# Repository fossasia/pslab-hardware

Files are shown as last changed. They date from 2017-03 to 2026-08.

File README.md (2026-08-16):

# pslab-hardware





This repository contains the [PSLab](https://pslab.io) hardware design files. PSLab is a tiny pocket science lab that provides an array of test and measurement instruments for doing science and engineering experiments. It can function like an oscilloscope, waveform generator, frequency counter, programmable voltage and current source and also as a data logger. The first version of hardware (v1) was developed by [Jithin](https://github.com/jithinbp). Later versions were developed by [Padmal](https://github.com/CloudyPadmal) and [Rafael](https://github.com/RafaelLeeImg).

## PCB Layout
Front Side                        | Back Side
 -------------------------------- | ----------------------------------
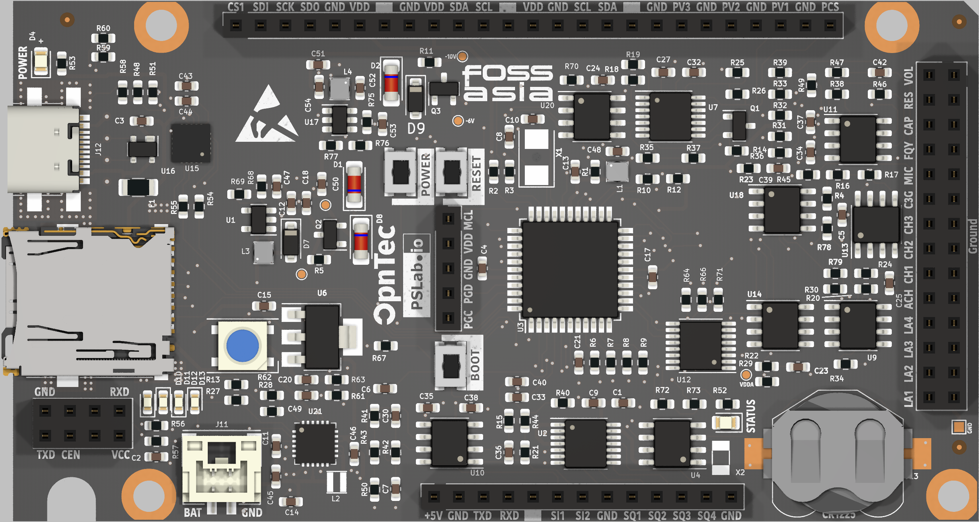
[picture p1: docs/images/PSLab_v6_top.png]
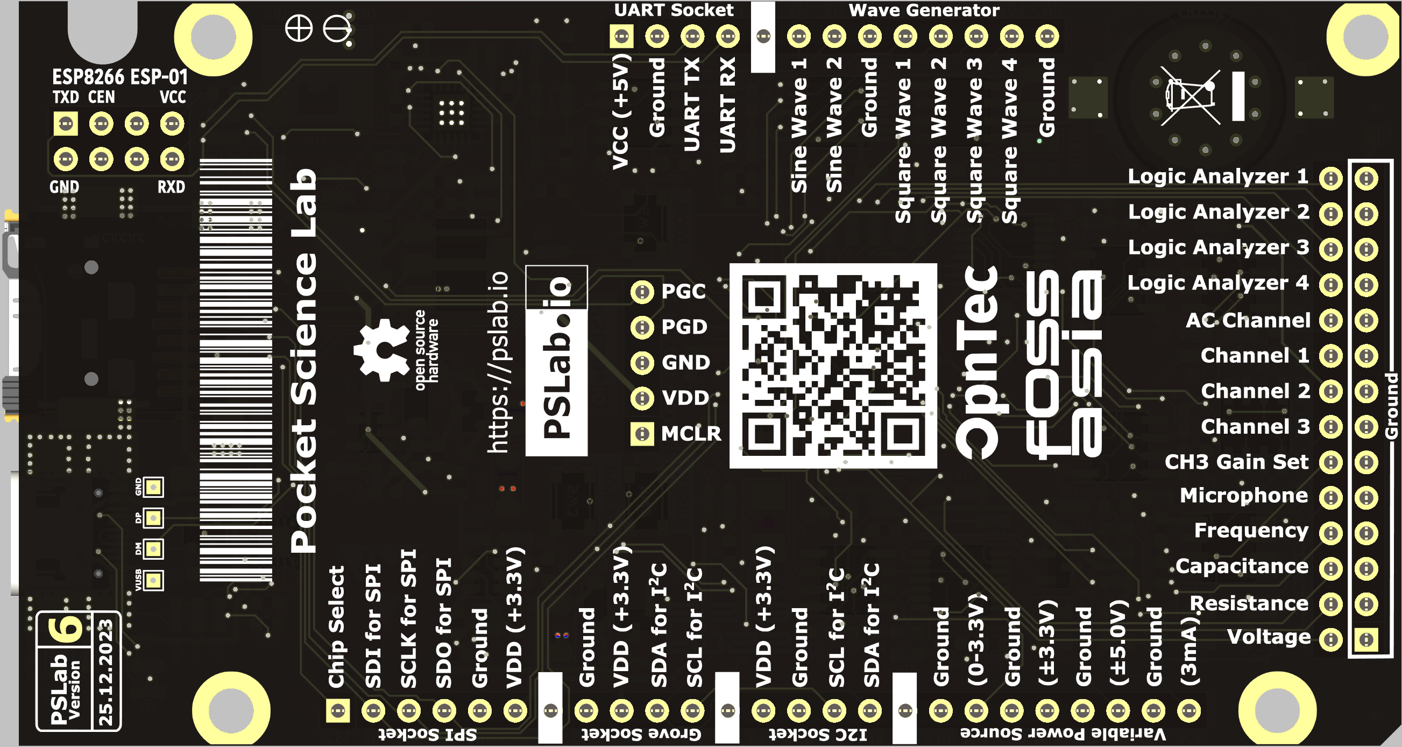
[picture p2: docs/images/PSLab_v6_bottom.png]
 | 

## Pin-outs
- Find the pin-out diagram of PSLab V6 [here](docs/pin_layouts/PSLab_Pin_Layout.pdf)!

## Applications and Firmware Source Repositories

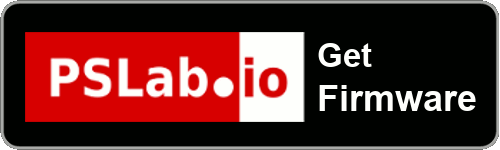
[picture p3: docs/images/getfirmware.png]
(https://github.com/fossasia/pslab-firmware)
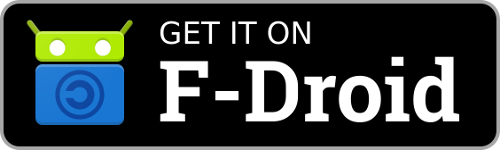
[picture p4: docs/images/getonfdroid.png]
(https://f-droid.org/en/packages/io.pslab/)
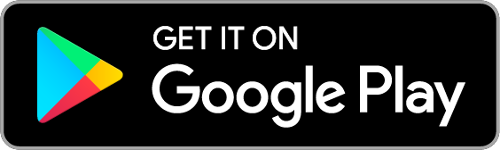
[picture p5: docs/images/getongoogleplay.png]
(https://play.google.com/store/apps/details?id=io.pslab)
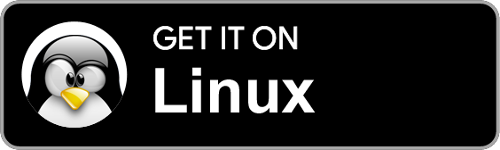
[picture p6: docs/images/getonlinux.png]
(https://github.com/fossasia/pslab-app/tree/app)
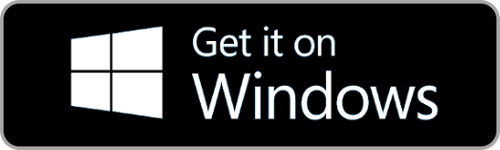
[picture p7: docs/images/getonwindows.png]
(https://github.com/fossasia/pslab-app/tree/app)
| 	|	| 	| 	| 	|
|---	|---	|---	|---	|---	|

The following software components are available:
* Bootloader: https://github.com/fossasia/pslab-bootloader
* Firmware: https://github.com/fossasia/pslab-firmware
* Python library: https://github.com/fossasia/pslab-python
* PSLab app: https://github.com/fossasia/pslab-app

## Buy Device

* You can get a Pocket Science Lab device from the [FOSSASIA Shop](https://fossasia.com).
* More resellers are listed on the [PSLab website](https://pslab.io/shop/).

## Communication

* Our chat channel is on Gitter here at [PSLab](https://gitter.im/fossasia/pslab)
* Mailing List https://groups.google.com/forum/#!forum/pslab-fossasia

## Repository Structure

```
📦pslab-hardware
 ┣ 📂archives                                   # Source files for previous PSLab versions
 ┃ ┣ 📂Breakout_Boards
 ┃ ┣ 📂PSLab KiCAD
 ┃ ┣ 📂PSLab KiCAD v2
 ┃ ┗ 📂PSLab KiCAD v3
 ┣ 📂docs                                       # Supplementary material
 ┃ ┣ 📂components
 ┃ ┃ ┣ 📜BillOfMaterials.csv                    # Component list
 ┃ ┃ ┗ 📜InteractiveBoM.html                    # Interactive version of BoM
 ┃ ┣ 📂datasheets                               # PDF datasheets for components used in PSLab
 ┃ ┣ 📂drawings                                 # CAD dimension drawings
 ┃ ┣ 📂images
 ┃ ┃ ┣ 📂pslab_version_previews
 ┃ ┃ ┣ 📜 ...
 ┃ ┃ ┗ 📜PSLab_v6_top.png
 ┃ ┣ 📂pin_layouts                              # Pin labels and specifications
 ┃ ┃ ┣ 📜PSLab_Pin_Layout.pdf
 ┃ ┃ ┗ 📜PSLab_Pin_Layout.svg
 ┃ ┣ 📂position_files
 ┃ ┃ ┗ 📜PositionFile.csv                       # Pick and place information
 ┃ ┣ 📂reference                                # TeX documentation (stale)
 ┃ ┗ 📂schematics
 ┃ ┃ ┗ 📜PSLab.pdf                              # Board schematic in PDF
 ┣ 📂output
 ┃ ┣ 📂Gerber                                   # Gerber files for the current board design
 ┃ ┗ 📂Images                                   # Images of the four copper layers
 ┣ 📂print                                      # Silk screen images
 ┃ ┣ 📂Back-Side-Images
 ┃ ┗ 📜Readme.md
 ┗ 📂schematics                                 # KiCAD project files
   ┣ 📂3DModels                                 # STEP 3D models
   ┣ 📂PSLab.pretty                             # Custom library files
   ┣ 📜 ...
   ┗ 📜PSLab.pro                                # Main project file
```

## Version Information

| Version | Content | Preview |
| -------------- | ------- | ------- |
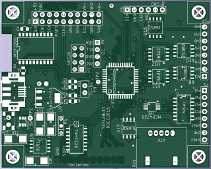
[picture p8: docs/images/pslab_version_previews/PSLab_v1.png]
| PSLab KiCAD v1   | Original version with `SEELABLET` schematics and layout files |  |
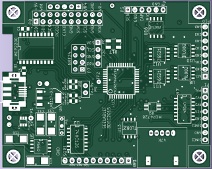
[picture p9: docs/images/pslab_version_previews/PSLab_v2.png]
| PSLab KiCAD v2 | Developed version with new additions (Voltage regulator, Oscillator) |  |
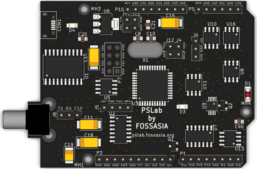
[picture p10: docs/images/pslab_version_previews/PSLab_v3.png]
| PSLab KiCAD v3 | Device layout changed to Arduino Uno form factor |  |
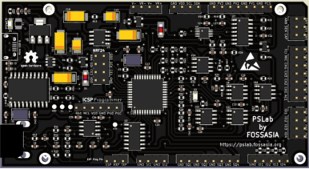
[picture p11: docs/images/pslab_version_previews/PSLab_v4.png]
| PSLab KiCAD v4 | Assembly optimized version with Arduino Mega form factor having components mounted only on top side |  |
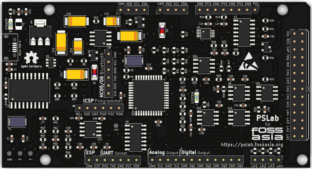
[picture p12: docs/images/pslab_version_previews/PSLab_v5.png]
| PSLab KiCAD v5 | Added socket for external bluetooth module and bottom silk screen with pin description |  |
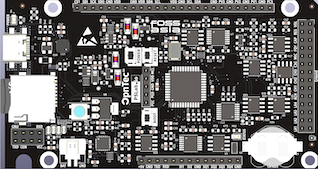
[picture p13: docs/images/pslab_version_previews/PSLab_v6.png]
| PSLab KiCAD v6 | Added external power input, RTC module, SD Card slot, USB type C, ESP 01 and upgraded UART and power ICs |  |

## Platform

* Microcontroller Platform : [PIC24EP256GP204](http://www.microchip.com/wwwproducts/en/PIC24EP256GP204)
* IDE: [MPLABX IDE v3.35](http://www.microchip.com/mplab/mplab-x-ide) (Supported on Linux/Windows/Mac)
* Compiler: [MPLAB® XC16 Compiler](http://www.microchip.com/mplab/compilers)
* Programming Tool: [PICkit™ 3 In-Circuit Debugger](http://www.microchip.com/Developmenttools/ProductDetails.aspx?PartNO=PG164130)

## Parts list

* [PIC24EP256GP204](http://www.microchip.com/wwwproducts/en/PIC24EP256GP204) - Microcontroller
* [MCP6S21](http://www.microchip.com/wwwproducts/en/mcp6s21) - Programmable gain amplifier
* [MCP4728](http://www.microchip.com/wwwproducts/en/mcp4728) - 4 Channel DAC
* [TC7660](http://www.microchip.com/wwwproducts/en/TC7660) - Charge Pump voltage invertor
* [TC1240A](http://www.microchip.com/wwwproducts/en/TC1240A) - Charge Pump voltage doubler
* [TL082](http://www.ti.com/product/TL082) - 2 channel Op-Amp
* [LM324](http://www.ti.com/product/LM324) - 4 channel Op-Amp
* [DS1307Z+](https://datasheets.maximintegrated.com/en/ds/DS1307.pdf) - RTC module
* [LDFM33PUR](https://www.st.com/resource/en/datasheet/ldfm.pdf) - 3.3 V regulator
* [LDL212PU50R](https://www.st.com/resource/en/datasheet/ldl212.pdf) - 5.0 V regulator
* [CP2102N-A02-GQFN24](https://www.silabs.com/documents/public/data-sheets/cp2102n-datasheet.pdf) - USB-UART bridge
* [74HC126](http://www.ti.com/product/SN74HC126) - 4 channel buffer
* [SP0503BAHTG](https://m.littelfuse.com/~/media/electronics/datasheets/tvs_diode_arrays/littelfuse_tvs_diode_array_sp05_datasheet.pdf.pdf) - ESD protector

* 0.5 A Fuse
* Assorted resistors, capacitors & diodes

Find the complete bill of materials from [this link](docs/components/BillOfMaterials.csv).

### Optional Parts

Extension slots for an ESP is available.
* [ESP8266 (ESP-01)](http://www.microchip.ua/wireless/esp01.pdf) - UART-TCP bridge

## Hardware Specs

* 3-Channel up to 2MSPS Oscilloscope. Software selectable amplification stages
* 12-bit Voltmeter with programmable gain. Input ranges from +/-10 mV to +/-16 V
* 3x 12-bit Programmable voltage sources +/-3.3 V,+/-5V,0-3 V
* 12-bit Programmable current source. 0-3.3 mA
* Supports Advanced plugins/Add-on Modules
* 4-Channel, 4 MHz Logic Analyzer
* 2x Sine/Triangular wave generators. 5 Hz to 5 KHz. Manual amplitude control for SI1
* 4x PWM generators. 15 nS resolution. Up to 8 MHz
* Capacitance Measurement. pF to uF range
* I2C, SPI and UART data buses for Accelerometer gyroscope humidity and temperature sensor modules etc

## Feature list for the acquisition and control

### Oscilloscopes

One of the main features of PSLab is the 3-channel Oscilloscope which can monitor analog inputs at maximum of 2 million samples per second. It includes controls such as triggering, and gain selection. Uses Python-Scipy for curve fitting.

### Waveform Generators

* SI1 : 5 Hz – 5 KHz arbitrary waveform generator. Manual amplitude control up to +/-3 Volts
* SI2 : 5 Hz – 5 KHz arbitrary waveform generator. Amplitude of +/-3 Volts. Attenuable via software
* SQx : There are four phase correlated PWM outputs with maximum frequency 32 MHz, 15 nano second duty cycle, and phase difference control.

### Measurement Functions

* Frequency counter tested up to 16 MHz.
* Capacitance Measurement. pF to uF range
* PSLab has several 12-bit analog inputs (function as voltmeters) with programmable gains, and maximum ranges varying from +/-5 mV to +/-16 V.

### Voltage and Current Sources

* 12-bit Constant Current source. Maximum current 3.3 mA (subject to load resistance).
* PSLab has three 12-bit Programmable voltage sources +/-3.3 V,+/-5 V,0-3 V. (PV1, PV2, PV3) controls

### Other useful tools

* 4MHz, 4-channel Logic analyzer with 15 nS resolution. Voltage and current sources
* SPI, I2C and UART outputs
* Graphical Interfaces for Oscilloscope, Logic Analyser, streaming data and several experiments developed that use a common framework which drastically reduces code required to incorporate control and plotting widgets.
* PSLab also has space for an ESP-01 module for WiFi access with access point/station mode.

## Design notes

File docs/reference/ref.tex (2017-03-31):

%----------------------------------------------------------------------------------------
%	PACKAGES AND OTHER DOCUMENT CONFIGURATIONS
%----------------------------------------------------------------------------------------

\documentclass[11pt,article,sans]{moderncv} % Font sizes: 10, 11, or 12; paper sizes: a4paper, letterpaper, a5paper, legalpaper, executivepaper or landscape; font families: sans or roman
\moderncvstyle{classic} % CV theme - options include: 'casual' (default), 'classic', 'oldstyle' and 'banking'
\moderncvcolor{blue} % CV color - options include: 'blue' (default), 'orange', 'green', 'red', 'purple', 'grey' and 'black'

\usepackage[scale=0.75]{geometry} % Reduce document margins

%\setlength{\hintscolumnwidth}{3cm} % Uncomment to change the width of the dates column
%\setlength{\makecvtitlenamewidth}{10cm} % For the 'classic' style, uncomment to adjust the width of the space allocated to your name

\usepackage{graphicx}
\usepackage{multicol}
\usepackage{changepage}

%----------------------------------------------------------------------------------------
%	NAME AND CONTACT INFORMATION SECTION
%----------------------------------------------------------------------------------------

\firstname{PSLab} % Your first name
\familyname{} % Your last name

\title{Technical Specifications}
\email{Mfd by. csparkresearch@gmail.com}
\address{www.fossasia.org}{}
\photo[100pt][0pt]{pictures/logo.png} % The first bracket is the picture height, the second is the thickness of the frame around the picture (0pt for no frame)

%----------------------------------------------------------------------------------------
\setlength\arrayrulewidth{.4pt}
\setlength\tabcolsep{6pt}

\begin{document}

\makecvtitle % Print the CV title

\chapter{\color{blue!50!green}\LARGE\bfseries Introduction}
\vspace{5mm}
\\.
\setlength{\parindent}{1cm}
\textit{\color{blue!20!black!80}PSLab provides an array of test equipment that includes an oscilloscope, waveform generators, frequency counters, Programmable voltage sources and many more for the curious ones among us. The measurement/control functions are accessible from the Python programming language and GUI applications are also available for a variety of science and engineering experiments. } .\\
\setlength{\parindent}{0cm}

%----------------------------------------------------------------------------------------
%	Pin definition section
%----------------------------------------------------------------------------------------

\vspace{20pt}
\chapter{\color{blue!50!green}\LARGE\bfseries Pin Definitions and Functions}
\section{Analog Inputs - Measure Voltages with 12-bit resolution}
\cventry{CH1}{Range:$\pm$ 16}{}{ Gain:up to 32x.}{ }{}{}
\cventry{CH2}{Range:$\pm$ 16}{}{ Gain:up to 32x.}{ }{}{}{}
\cventry{CH3}{Range:$\pm$ 3.3V}{}{}{}{*manual gain control by grounding Rg via resistor R  . $gain = 1 + \frac{10K}{R_g}$}{}
\cventry{MIC}{Range: $\pm15mV$}{}{}{ Gain:200x.}{}{}
\cventry{SEN}{Range: $0 - 3.3V$}{}{}{ Internally Pulled up to 3.3V via 5.1KOhm resistor}{}{}

\section{Analog Outputs}
\subsection{Waveform Generators}
\cventry{WG1}{5Hz to 5KHz Arbitrary Waveform Generator}{Range: $ \pm 3V$ .Attenuable}{}{}{}{}
\cventry{WG2}{5Hz to 5KHz Waveform Generator}{Range: $ \pm 3V$  }{}{}{}{}
\subsection{Programmable Voltage and Current Sources (12-bit)}
\cventry{PVS1}{Range: $ \pm 5V$}{}{Up to 10mA}{}{}{}
\cventry{PVS2}{Range: $ \pm 3.3V$}{}{Up to 10mA}{}{}{}
\cventry{PVS3}{Range: $0 - 3.3V$}{}{Up to 10mA}{}{}{}
\cventry{PCS}{Range: $0 - 3.3mA$}{}{}{}{Subject to Load resistance. Up to 3.3V voltage drop}{}

\section{Digital Inputs - Measure Logic Levels with 15nS resolution}
\subsection{Logic Analyzer, Frequency Counter, Timing Functions}
\cventry{ID1}{Range: $0 - 5V$}{}{0-32MHz}{}{}{}
\cventry{ID2}{Range: $0 - 5V$}{}{0-32MHz}{}{}{}
\cventry{ID3}{Range: $0 - 5V$}{}{0-32MHz}{}{}{}
\cventry{ID4}{Range: $0 - 5V$}{}{0-32MHz}{}{}{}
\cventry{Fin}{Range: Up to $\pm5V$}{}{0-16MHz}{}{}{}

\section{Digital Outputs }
\subsection{4x PWM output with 15nS frequency, phase, and DCycle control}
\cventry{SQR1}{Range: $0 - 5V$}{}{}{}{}{}
\cventry{SQR2}{Range: $0 - 5V$}{}{}{}{}{}
\cventry{SQR3}{Range: $0 - 5V$}{}{}{}{}{}
\cventry{SQR4}{Range: $0 - 5V$}{}{}{}{}{}

\section{Data Buses - I2C , SPI, UART}
\subsection{I2C (Inter-Integrated Circuit) Master: Up to 4MHz Clock speed}
\cventry{Vdd}{3.3V Power output}{}{}{}{}{}
\cventry{GND}{Return path}{}{}{}{}{}
\cventry{SCL}{I2C Clock Output}{}{}{}{}{}
\cventry{SDA}{I2C Data Line}{}{}{}{}{}

\subsection{SPI(Serial-Peripheral Interface) Master: Available on the 20-pin Expansion Slot. Supports all four modes of operation.}
\cventry{SCK}{SPI Clock Output}{}{Tested Up To 16MHz}{}{}{}
\cventry{SDO}{SPI Data Output (MOSI)}{}{}{}{}{}
\cventry{SDI}{SPI Data Input (MISO)}{}{}{}{}{}
\cventry{CS1}{Chip Select 1}{}{}{}{}{}
\cventry{CS2}{Chip Select 2}{}{}{}{}{}

\section{A Few Definitions For The Expansion slot}
\cventry{CLK}{16MHz , 0-3.3V TTL output}{}{This is also the reference clock for the 0-2MHz sine/triangle wave generator, and can be used to create phase correlated wavegen add-ons}{}{}{}
\cventry{AN8}{Analog Input}{}{Range: $0 - 3.3V$}{}{}{}

\section{Additional Nomenclature }
\cventry{GND}{Short for GROUND.}{}{This is the reference voltage, and is taken as 0 volts}{}{It is also connected to the ground level of the power source (power adapter)}{}
\cventry{V+/V-}{Power Outputs}{}{$\pm 9V$ . Current limit 20mA per channel}{}{}{}

\pagebreak
\vspace{20pt}
\chapter{\color{blue!50!green}\LARGE\bfseries Sensors and Add ons}\\

\section{Plug and Play Sensors}

\begin{adjustwidth}{7em}{0pt}

\begin{itemize}
\item MPU6050 : 3-Axis Accelerometer , 3-Axis GyroScope, temperature sensor
\item HMC5883L : 3-Axis Magnetometer with adjustable ranges
\item MLX90614 : Passive IR temperature sensor
\item BMP180 : Pressure , Temperature and Altitude module.
\item TSL2561 : Luminosity measurements up to 40K Lux
\item BH1750 : Luminosity measurements up to 40K Lux
\item SHT21 , Si7021 : Ambient Temperature and Humidity Module
\item SSD1306 : 128x64 OLED Display
\item HCSR501 : Passive IR module for motion sensing
\item AD9833 : 28-bit DDS function generator
\item PT100 temperature sensor, MQ Series Gas sensors
\item DSM501 : PM2.5 Dust Sensor
\item YL-69 : Hygrometer for soil humidity measurements
\item WS2812B RGB LED with 16 million shades 
\item HX711 24-bit differential ADC with 128x PGA
\item MFRC522 : RFID Reader
\item HB100 : 10.25GHz Doppler Radar
\end{itemize}
\end{adjustwidth}

\section{Wireless Subunits : 3-Byte addresses [ Purchase separately]}

PSLab has an On-board Transceiver (2-way radio link) Capable of communicating with multiple wireless nodes to control and receive sensor data payloads.\\ These wireless nodes are drop-in replacements for sensors, and have a typical line of sight range of 50 meters.

\begin{center}

%  \includegraphics[width=0.6\linewidth]{pictures/node_case.jpg}

\end{center}

\cventry{I2C}{Data bus for Interfacing with commonly available sensors.}{ Measure physical parameters with minimal mechanical interference}{}{}{}
\cventry{SPI}{Two Chip select pins}{}{}{}{}
\cventry{RGB out}{Control WS2812B arrays }{}{Daisy chained RGB LEDs with 16 million shades each}{}{}{}

\section{Control And Measurement Equipment Specifications}

\textit{\color{blue!50!green}Calibrated Against Professional equipment for high accuracy}\\
\begin{tabular}{|l|l|l|l}
\hline
\multicolumn{1}{|c|}{{\color[HTML]{9A0000} \textbf{Feature}}}          & \multicolumn{1}{c|}{{\color[HTML]{9A0000} \textbf{Description}}}                                                                                                                                                                                                                                                                                                             & \multicolumn{1}{c|}{{\color[HTML]{9A0000} \textbf{Socket Labels}}}                            & \multicolumn{1}{c}{{\color[HTML]{9A0000} \textbf{Range}}}                                                                                                            \\ \hline
\textbf{Analog Inputs}                                                 & \begin{tabular}[c]{@{}l@{}}Up to 6 analog inputs with various voltage ranges.\\ Programmable gain control.\\ 12-bit voltage measurement. Up-to 2MSPS sampling.\\ $3.3V$ Voltage Reference\\ \\ .\end{tabular}                                                                                                                                                    & \begin{tabular}[c]{@{}l@{}}CH1, CH2\\ CH3\\ MIC\\ SEN\end{tabular}                            & \multicolumn{1}{l|}{\begin{tabular}[c]{@{}l@{}}$\pm16 Volts$\\ $\pm3.3 Volts$\\ $\pm15m V V$\\ $0-3.3 V$\end{tabular}}                                               \\ \hline
\textbf{Analog Outputs}                                                & \begin{tabular}[c]{@{}l@{}}Programmable Voltage Sources (12-bit)\\ \\ \\ Programmable Constant Current Source\\ .\end{tabular}                                                                                                                                                                                                                                               & \begin{tabular}[c]{@{}l@{}}PVS1\\ PVS2\\ PVS3\\ PCS\\ .\end{tabular}                          & \multicolumn{1}{l|}{\begin{tabular}[c]{@{}l@{}}$\pm5 V$\\ $\pm3.3 V$\\ $0-3.3 V$\\ $0-3.3 mA$\\ .\end{tabular}}                                                      \\ \hline
\textbf{Digital Inputs}                                                & \begin{tabular}[c]{@{}l@{}}4 x TTL compatible digital Inputs. \\ Logic Analyzer\\ Frequency Counter (0-16MHz), \\ time measurement routines\\ \textit\{$\pm30ppm , 12MHz$ Reference oscillator\}\end{tabular}                                                                                                                                                               & \begin{tabular}[c]{@{}l@{}}ID1 - ID4\\ \\ Fin\end{tabular}                                    & \multicolumn{1}{l|}{\begin{tabular}[c]{@{}l@{}}$0-5$ V\\ \\ $0-\pm5 V$\end{tabular}}                                                                                 \\ \hline
\textbf{\begin{tabular}[c]{@{}l@{}}Waveform\\ Generators \end{tabular}} & \begin{tabular}[c]{@{}l@{}}Wavegen 1 (Sine/Triangle/Arbitrary)\\ -Frequency\\ -Amplitude. Manually attenuable \\ \\ Wavegen 2 (Sine/Triangle/Arbitrary)\\ --Frequency\\ -Amplitude. Fixed\\ \\ 4 x Phase Correlated Square Waves\\ -Frequency\\ -Phase difference maximum resolution\\ -Duty Cycle maximum resolution\\ -Also functions as simple state selectable output.\\ -servo/stepper motor control supported\end{tabular} & \begin{tabular}[c]{@{}l@{}}W1\\ \\ \\ \\ W2\\ \\ \\ \\ SQ1 - SQ4\\ \\ \\ \\ \\ .\end{tabular} & \multicolumn{1}{l|}{\begin{tabular}[c]{@{}l@{}}\\ $5-5K$Hz\\ $\pm3 V$\\ \\ \\ $5-5K$Hz\\ $\pm3 V$\\ \\ \ \\ $0-5 Volts$\\10Hz - 16MHz\\ 15nS\\ 15nS\\ \\ \\ .\end{tabular}} \\ \hline
\textbf{Data Buses}                                                    & \begin{tabular}[c]{@{}l@{}}I2C : Master\\ Commonly Used by numerous sensor ICs\\ SPI : Master\\ -Chip Select pins\\ UART \\ .\end{tabular}                                                                                                                                                                                                                                   & \begin{tabular}[c]{@{}l@{}}SCL,SDA\\ \\ SCK,SDI,SDO\\ CS1 , CS2\\ \\ .\end{tabular}           & \multicolumn{1}{l|}{}                                                                                                                                                \\ \hline
\textbf{Expansion Slot}                                                & \begin{tabular}[c]{@{}l@{}}20 - pin Socket designed to accommodate\\  add-on modules.\\ -Selection includes SPI,I2C,Analog input,Digital IO,\\ 16MHz TTL output, and a bipolar power supply.\end{tabular}                                                                                                                                                                       &                                                                                               & \multicolumn{1}{l|}{}                                                                                                                                                
\\ \hline
\textbf{Wireless Nodes}                                                & \begin{tabular}[c]{@{}l@{}}Battery Powered add-on units.\\ Power Source\\ -Acts as a wireless bridge for various sensors\\ 3 Byte unique address\\ -10 bit ADC , Digital I/O\\ .\end{tabular}                                                                                                                                                & \begin{tabular}[c]{@{}l@{}}.\\ Cell/Adapter\\ \\ \\ \\ .\end{tabular}                         & \multicolumn{1}{l|}{\begin{tabular}[c]{@{}l@{}}.\\ 3.7-4.2 V\\  \\  \\ \\ .\end{tabular}}                                                                            
\\ \hline

\end{tabular}

\pagebreak

%\section{Data acquisition and control software}
%The Following is an evolving list of graphical applications that have been installed along with the Python module, and can accessed by launching applications->education->PSLab.\\
%\cventry{1}{Oscilloscope}{}{Max 2MSPS, Up to 4-channel oscilloscope}{Features : Sine,Square fitting and overlay, Fourier transform, trigger selection, X-Y mode, gain control}{}
%\cventry{2}{Data Streaming}{}{Generic data logger for functions defined in the Python library}{}{}
%\cventry{3}{Sensor Data logger}{}{Data logger for plugged in add-on modules supported in the python library such as accelerometers, gyros and luminosity sensors}{}{For the complete list, refer to the Sensors and Add ons section}
%\cventry{4}{Transistor CE}{}{Study common emitter characteristics of transistors}{}{}
%\cventry{5}{Diode IV}{}{Study Current-Voltage characteristics of PN junctions}{}{}
%\cventry{6}{servo motors}{}{Control up to 4 servo motors via the PWM outputs}{}{}
%\cventry{7}{Stepper motors}{}{ Control 4-wire stepper motors.}{}{}
%
%
%\pagebreak

\chapter{\color{blue!50!green}\LARGE\bfseries \color{blue!50!black!80}Data Acquisition and control software}\\
\\
Launch the PSLab Application , launch the oscilloscope utility listed in the \textit{Test and Measurement} section
\section{Control widgets  }
\subsection{Voltage and current sources}
\cventry{PVS1}{Range : $\pm5V$}{Set the output voltage on PVS1 socket.}{ Max Current 5mA}{}{}
\cventry{PVS2}{Range : $\pm3.3V$}{Set the output voltage on PVS2 socket.}{ Max Current 5mA}{}{}
\cventry{PVS3}{Range : $0-3V$}{Set the output voltage on PVS3 socket.}{ Max Current 5mA}{}{}
\cventry{PCS}{Range : $0-3.3mA$}{Set the output current on PCS socket. Current subject to load resistance}{}{PCS and PVS3 are linked, and only one can be used at a time}{}

\subsection{Arbitrary Waveform Generators (W1,W2)}
\cventry{W1}{Range : $5Hz-5KHz$}{Set the output frequency of the waveform generator.}{}{Amplitude control($\pm1mV-\pm3V$) via physical knob located on the device}{}
\cventry{W2}{Range : $5Hz-5KHz$}{Set the output frequency of the waveform generator.}{}{Fixed amplitude 3V}{}

\subsection{Phase Correlated Square Waves (SQ1,SQ2,SQ3,SQ4)}

\cventry{Frequency}{Range : $0-8MHz$}{Set the output frequency of all four square waves.}{ Resolution:$15nS$}{}{}
\cventry{Output}{Select the Output socket to configure}{}{}{}{}
\cventry{Phase}{Set the phase difference ($0-100\%$) }{}{between the selected waveform and SQ1}{}{}
\cventry{Duty Cycle}{Set the Duty Cycle($0-100\%$)  }{}{of the selected waveform}{}{}

\vspace{10mm}

\chapter{\color{blue!50!green}\LARGE\bfseries \color{blue!50!black!80}Oscilloscope }\\
\\
From the PSLab Application , launch the oscilloscope utility listed in the \textit{Test and Measurement} section
\subsection{Chan 1 : Channel 1 of the oscilloscope}
\cventry{Remappable}{Not restricted to 'CH1' input socket.}{ This is a very flexible acquisition channel, and can be mapped to any of the analog inputs via a drop down menu located at the top corner}{}{}{}
\subsection{Chan 2 : Channel 2 of the oscilloscope}
\cventry{Fixed}{This channel can only record the signals input to the socket labelled CH2}{}{}{}{}

\subsection{TRIGGER : Allows selecting the channel to trigger the oscilloscope}
\cventry{Level}{The rotary dial sets the trigger level, and this is also reflected in a marker located on the plot}{}{}{}{}
\cventry{Channel}{The drop down menu allows selecting the trigger channel}{}{}{If CH1 is selected, the trigger signal will be obtained from the channel it has been mapped to}{}

\subsection{TimeBase : Specify the time scale for the data acquisition}
\cventry{Dial}{Set the delay(in uS) between each successive data point}{}{}{}{}

\subsection{Sine Fit :Uses Scipy to fit the data against a sine function}
\cventry{Menu 1}{Select input data channel for fitting}{}{}{Uses Scipy.optimize and obtains frequency, amplitude, phase and offset values}{}
\cventry{Menu 2}{Select a second input data channel for fitting}{}{}{}{}
\cventry{checkbox}{Overlay the fitted results}{}{}{}{}
\cventry{Results}{The fitted values: Amplitude, Freq, Phase( and phase difference), Offset are displayed in the message window at the bottom of the screen}{}{}{}{}

\subsection{Lissajous : XY Plots}
\cventry{Menu 1}{Select input data channel for X-axis}{}{}{}{}
\cventry{Menu 2}{Select input data channel for Y-axis}{}{}{}{}

\vspace{10mm}

\pagebreak
\chapter{\color{blue!50!green}\LARGE\bfseries \color{blue!50!black!80}Wireless Submodules}\\
\\
From the PSLab Application , launch the wireless-sensors utility listed in the \textit{Test and Measurement} section\\
\begin{center}

%  \includegraphics[width=\linewidth]{pictures/wireless-demo.png}
%Screenshot of the wirelessDemo application
\end{center}

\section{Interfacing a new wireless submodule carrying a sensor}
\cventry{1}{Plug in a supported sensor on to a wireless node by matching the pins labelled $Vdd,GND,SCL,SDA$ . These pins appear in the same order on most sensor modules, and no extra wires should be needed}{}{}{}{}
\cventry{2}{}{}{Make sure that the option \textit{Listen for nodes} on the Application is selected}{}{}
\cventry{3}{}{}{Plug In the Battery onto the wireless node/ Turn on the node.}{}{}
\cventry{4}{}{}{Observe that the software has auto detected your wireless node as well as found out the address of the sensor you connected.}{}{}
\cventry{5}{}{}{Unselect \textit{Register New Nodes}}{}{If you wish, you may move the cursor over a sensor's address and the software will guess its model number/type}
\cventry{6}{Click on }{}{\textit{Refresh Node List}}{This loads a few controls for each wireless node, and also a drop down selection of the connected sensors}{}

\section{Logging Data from a sensor}
\cventry{1}{After Following the steps in the previous section}{}{Select the appropriate sensor and click on \textit{Go}}{The software will continuously plot values fetched from the sensor}{}
\section{Changing sensor parameters}
\cventry{1}{Open the auto-generated menu at the bottom left corner}{}{and change parameters.}{A few examples include gain, sampling rates, and datatype selection}{}

\pagebreak
\chapter{\color{blue!50!green}\LARGE\bfseries \color{blue!50!black!80} Data logger Application}\\
\\
This application plots the return values from any of the functions defined in the Python Module as long as they return integers or decimals.\\
\\
From the PSLab Application , launch the \textit{data streaming} utility listed in the \textit{Test and Measurement} section
\begin{center}

%  \includegraphics[width=\linewidth]{pictures/streamapp.png}
%Screenshot of the streaming application.
\end{center}

\section{Choosing a command and starting the logger}
\cventry{1}{Refer to the programmer's manual for a list of valid commands}{}{and pick the function you would like to monitor}{}{}
\cventry{2}{Paste the command name with correct arguments into the application.}{}{And now click on \textit{Monitor}}{This app also includes a few common commands and appropriate arguments packed into a drop down menu linked to the command entry box}{}

\section{Additional Functionality Accessible through menus}
\cventry{Voltmeter}{Load Widgets that perform a single voltage measurement per click}{}{}{}{}
\cventry{Amplifiers}{Load a widget to set the gain on the voltage input channels}{}{}{}{}
\cventry{Wavegen}{Load a slider that allows setting the frequency of the sine wave output}{}{}{}{}
\cventry{IV sources}{Load widgets that}{}{enable setting programmable voltage and current}{}{}
\cventry{Timing}{Load time measurement widgets}{}{}{These include duty cycle and frequency}{}
\cventry{Console}{Insert an iPython Console with init commands preloaded}{}{}{}{}
\cventry{help}{Help menu that allows access to the programmer's manual as well as experiment specific HTML files}{}{}{}{}

\end{document}

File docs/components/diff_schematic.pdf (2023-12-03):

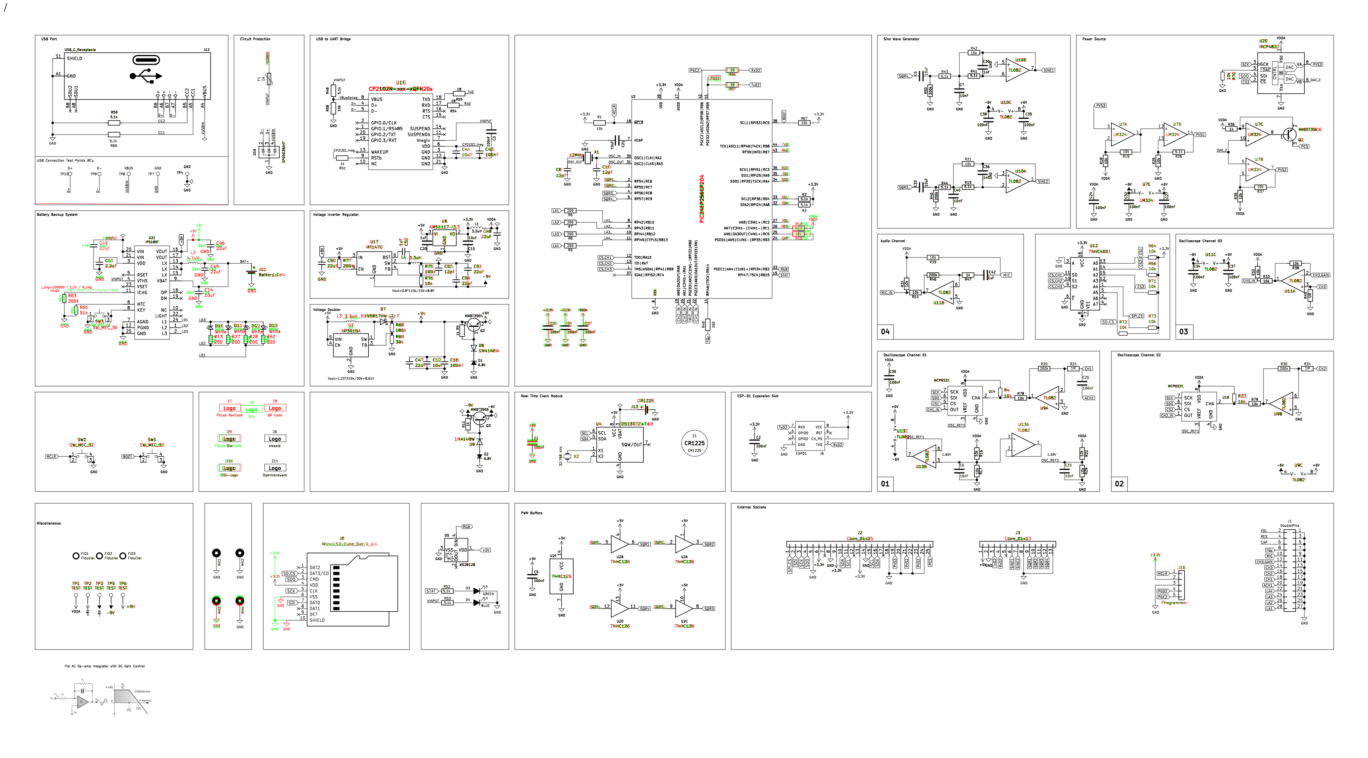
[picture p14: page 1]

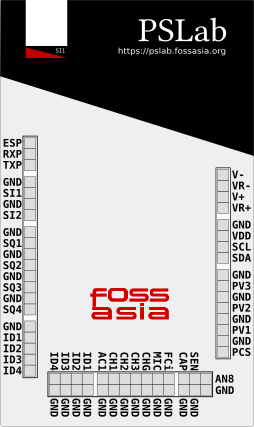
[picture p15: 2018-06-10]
docs/images/pslabdesign.png

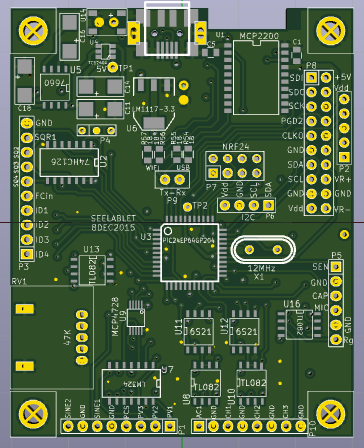
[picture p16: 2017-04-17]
docs/images/layout_front.png

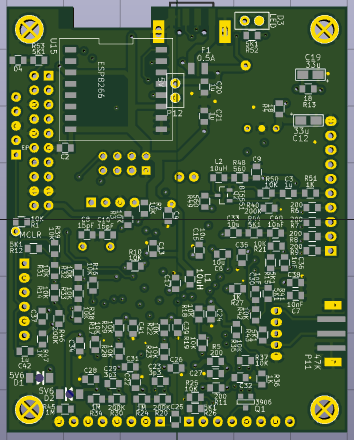
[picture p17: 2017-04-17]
docs/images/layout_back.png

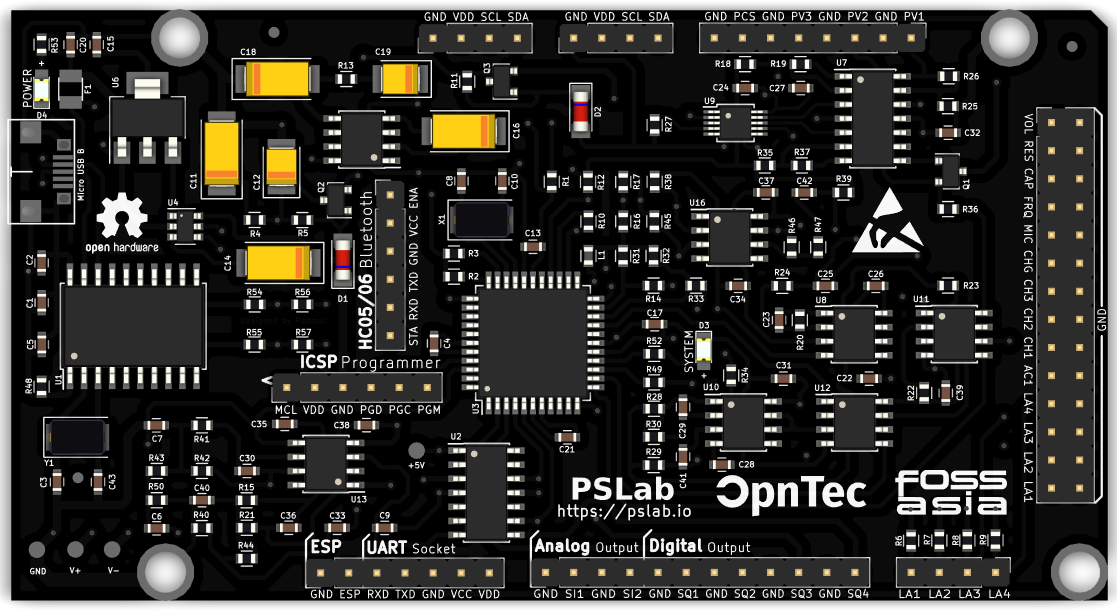
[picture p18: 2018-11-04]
docs/images/PSLab_v5_top.png

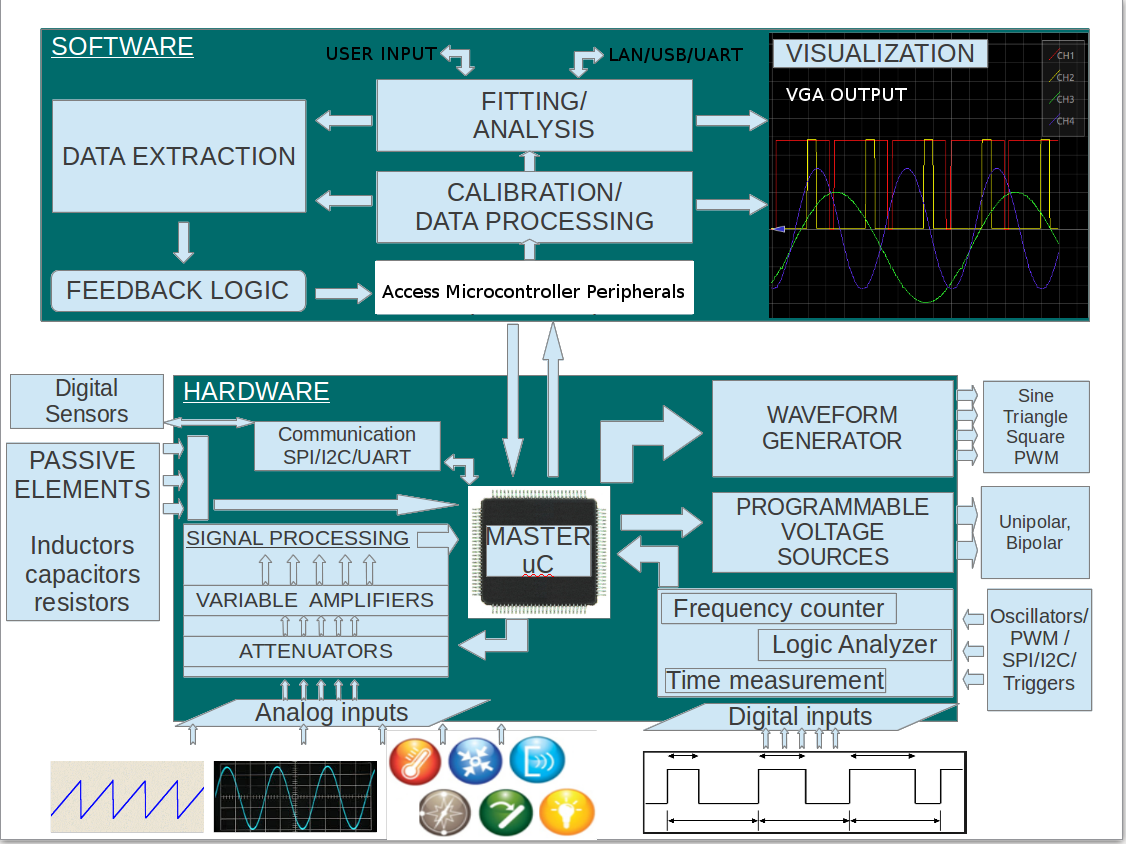
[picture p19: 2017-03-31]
docs/images/blockdiag.png

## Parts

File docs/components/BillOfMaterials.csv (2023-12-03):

References | Value | Footprint | Quantity | PartNumber | Price | Datasheet | Description
C8 C10 C53 | 12pF | C_0603_1608Metric | 3 |  |  | 10V 10% | Unpolarized capacitor, small symbol
C30 C36 | 1nF | C_0603_1608Metric | 2 | C0603C102J5RACAUTO | 0.12 | https://eu.mouser.com/datasheet/2/212/KEM_C1023_X7R_AUTO_SMD-1093309.pdf | 16V 5%
C5 C7 C23 C40 | 10nF | C_0603_1608Metric | 4 | C0603C104J4RACTU VJ0603Y103JXJPW1BC | 0.15 0.37 | https://eu.mouser.com/datasheet/2/212/KEM_C1002_X7R_SMD-1102033.pdf | 16V 10% 16V 5%
C1 C2 C3 C4 C9 C13 C17 C18 C24 C25 C27 C32 C34 C35 C37 C38 C39 C43 | 100nF | C_0603_1608Metric | 18 | C0603C104J4RACTU | 0.15 | https://eu.mouser.com/datasheet/2/212/KEM_C1002_X7R_SMD-1102033.pdf | 16V 10%
C20 C42 C52 | 1uF | C_0603_1608Metric | 3 | 0603YD105KAT2A | 0.18 | https://eu.mouser.com/datasheet/2/40/cx5r-776519.pdf | 16V 20%
C11 | 2.2uF | C_0603_1608Metric | 1 |  |  | 10V CL10A225KP8NNNC | Unpolarized capacitor, small symbol
C6 C12 C14 C15 C21 C33 C44 | 10uF | C_0603_1608Metric | 7 | EMK107BC6106MA-T | 0.46 | https://eu.mouser.com/datasheet/2/396/mlcc02_e-1307760.pdf | 16V 20%
C45 C46 C47 C48 C49 C50 C51 C54 | 22uF | C_0603_1608Metric | 8 |  |  | 10V | Unpolarized capacitor, small symbol
D8 | 1N4148W | D_MiniMELF | 1 |  |  | ~ | Diode
D9 | 1N4148W | D_SOD-123 | 1 |  |  | https://www.vishay.com/docs/85748/1n4148w.pdf | 75V 0.15A Fast Switching Diode, SOD-123
D1 D2 | 6.8V | D_MiniMELF | 2 | BZV55B6V8 L1 | 0.23 | ~ | 6.8V Zener
D4 | BLUE | LED_0805_2012Metric | 1 | HSMR-C170-R0000 | 0.85 | ~ | Blue 0805
D3 | GREEN | LED_0805_2012Metric | 1 | HSMQ-C170-T0000 | 0.94 | ~ | Green 0805
D7 | K1N5817HW-7-F | D_SOD-123 | 1 |  |  | ~ | Schottky diode
D5 | WS2812B | LED_WS2812B_PLCC4_5.0x5.0mm_P3.2mm | 1 | WS2812B | 3.35 | https://www.mouser.fi/datasheet/2/737/4684_WS2812B_2020_V1_3_EN-1900866.pdf | RGB LED with integrated controller
D10 D11 D12 D13 | White | LED_0603_1608Metric | 4 |  |  | ~ | Light emitting diode, small symbol
F1 | 1A | Fuse_1206_3216Metric | 1 | 0ZCJ0025FF2E | 0.11 | https://www.mouser.fi/datasheet/2/240/Littelfuse_PTC_1812L_Datasheet.pdf-693388.pdf | Hold 250mA, Trip 500mA
J11 | Battery_Cell | 2.0mm_connector_edge | 1 |  |  | ~ | Single-cell battery
J13 | CR1225 | BatteryHolder_A359 | 1 | BAT-HLD-012-SMT | 0.29 | ~ | Coin cell battery holder (CR1225/1216)
J3 | Conn_01x13 | PinSocket_1x13_P2.54mm_Vertical | 1 |  |  | ~ | Generic connector, single row, 01x13, script generated (kicad-library-utils/schlib/autogen/connector/)
J2 | Conn_01x25 | PinSocket_1x25_P2.54mm_Vertical | 1 |  |  | ~ | Generic connector, single row, 01x25, script generated (kicad-library-utils/schlib/autogen/connector/)
J1 | DoublePins | PinSocket_2x14_P2.54mm_Vertical | 1 | SSW-114-01-T-D | 2.28 | https://eu.mouser.com/datasheet/2/527/ssw_th-1507658.pdf | Straight female 2.54 mm 2row
J6 | ESP01 | ESP-01 | 1 | SSW-104-01-T-D | 0.98 | https://eu.mouser.com/datasheet/2/527/ssw_th-1507658.pdf | Straight female 2.54 mm 2row
J8 | Micro_SD_Card_Det_9_pin | TF-015 | 1 |  |  | https://www.hirose.com/product/en/download_file/key_name/DM3/category/Catalog/doc_file_id/49662/?file_category_id=4&item_id=195&is_series=1 | Micro SD Card Socket with card detection pins
J10 | Programmer | PinSocket_1x05_P2.54mm_Vertical | 1 |  |  |  | Generic connector, single row, 01x05, script generated (kicad-library-utils/schlib/autogen/connector/)
J12 | USB_C_Receptacle | USB_C_Receptacle_12pin_SMT | 1 | U262-161N-4BVC11 | 0.32 | https://www.usb.org/sites/default/files/documents/usb_type-c.zip | USB - Type C Female 16 SMT
L1 L3 L4 | 3.3uH | L_Taiyo-Yuden_MD-2020 | 3 |  | 0.17 | https://atta.szlcsc.com/upload/public/pdf/source/20210810/8C07D4BA256EC9B57FF3FBBF0FDAC34D.pdf?Expires=4070880000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 | Inductor
L2 | 4.7uH | L_Taiyo-Yuden_MD-2020 | 1 |  |  | https://item.szlcsc.com/992539.html SMNR201610-4R7MT | Inductor, small symbol
Q2 | MMBT3904 | SOT-23 | 1 | MMBT3904,215 | 0.1 | https://eu.mouser.com/datasheet/2/916/MMBT3904-1599187.pdf | 45V Vce, 0.8A Ic, NPN, SOT-23
Q1 | MMBT3906 | SOT-23 | 1 | MMBT3906-7-F | 0.11 | https://www.onsemi.com/pdf/datasheet/pzt3906-d.pdf | 45V Vce, 0.8A Ic, PNP, SOT-23
Q3 | MMBT3906 | SOT-23 | 1 | MMBT3906-7-F | 0.11 | https://eu.mouser.com/datasheet/2/115/ds30059-15980.pdf | 45V Vce, 0.8A Ic, PNP, SOT-23
R54 R55 R56 R57 | 18 | R_0603_1608Metric | 4 | RR0816Q-180-D | 0.1 | https://eu.mouser.com/datasheet/2/392/susumu_RR_Data_Sheet-1206438.pdf | 1/16W 5%
R6 R7 R8 R9 R13 R27 R28 R49 R62 | 200 | R_0603_1608Metric | 9 | RR0816P-201-D | 0.1 | https://eu.mouser.com/datasheet/2/392/susumu_RR_Data_Sheet-1206438.pdf | 1/16W 5%
R5 R11 R36 R47 R51 | 1k | R_0603_1608Metric | 5 | RR0816P-102-D | 0.12 | https://eu.mouser.com/datasheet/2/392/susumu_RR_Data_Sheet-1206438.pdf | 1/16W 5%
R2 R3 R12 R15 R26 R41 R43 R44 R48 R52 R53 R59 R60 | 5.1k | R_0603_1608Metric | 13 | RR0816P-512-D | 0.1 | https://eu.mouser.com/datasheet/2/392/susumu_RR_Data_Sheet-1206438.pdf | 1/16W 5%
R1 R4 R10 R14 R16 R17 R18 R19 R21 R23 R25 R29 R31 R32 R33 R35 R37 R38 R39 R42 R58 R64 R66 R67 R70 R71 R72 R73 R76 R78 R79 | 10k | R_0603_1608Metric | 31 | RR0816P-103-D | 0.12 | https://eu.mouser.com/datasheet/2/392/susumu_RR_Data_Sheet-1206438.pdf | 1/16W 5% 1/16W 1%
R22 | 12k | R_0603_1608Metric | 1 | RR0816P-103-D | 0.12 | https://eu.mouser.com/datasheet/2/392/susumu_RR_Data_Sheet-1206438.pdf | 1/16W 1%
R69 | 30k | R_0603_1608Metric | 1 |  |  | 1/16W 1% | Resistor, small symbol
R61 | 51k | R_0603_1608Metric | 1 |  |  | ~ | Resistor, small symbol
R75 | 100k | R_0603_1608Metric | 1 |  |  | ~ | Resistor, small symbol
R68 | 180k | R_0603_1608Metric | 1 |  |  | 1/16W 1% | Resistor, small symbol
R20 R30 R40 R46 R50 R63 R77 | 200k | R_0603_1608Metric | 7 | RR0816P-204-D | 0.1 | https://eu.mouser.com/datasheet/2/392/susumu_RR_Data_Sheet-1206438.pdf | 1/16W 5%
R24 R34 R45 | 1M | R_0603_1608Metric | 3 | RT0603FRE071ML | 0.1 | https://www.mouser.fi/datasheet/2/447/PYu-RT_1-to-0.01_RoHS_L_11-1669912.pdf | 1/16W 5%
SW1 SW2 SW3 | SW_MEC_5E | button_SPST_3x4x2.5 | 3 |  |  | http://www.apem.com/int/index.php?controller=attachment&id_attachment=1371 | MEC 5E single pole normally-open tactile switch
U2 | 74HC126 | TSSOP-14_4.4x5mm_P0.65mm | 1 | SN74HC126PW | 0.42 | http://www.ti.com/general/docs/suppproductinfo.tsp?distId=26 | TSSOP-14
U12 | 74HC4051 | TSSOP-16_4.4x5mm_P0.65mm | 1 |  |  | http://www.ti.com/lit/ds/symlink/cd74hc4051.pdf | 8-channel analog multiplexer/demultiplexer, DIP-16/SOIC-16/TSSOP-16
U6 | AMS1117-3.3 | SOT-223-3_TabPin2 | 1 |  |  | http://www.advanced-monolithic.com/pdf/ds1117.pdf | 1A Low Dropout regulator, positive, 3.3V fixed output, SOT-223
U1 | AP3015A | SOT-23-5 | 1
U15 | CP2102N-xxx-xQFN20x | QFN-20_EP_3x3_Pitch0.5mm | 1 |  |  | https://www.silabs.com/documents/public/data-sheets/cp2102n-datasheet.pdf
U4 | DS1307Z+T&R | SOIC-8_3.9x4.9mm_P1.27mm | 1 | DS1307Z+ | 3.69 | https://eu.mouser.com/datasheet/2/256/DS1307-1513036.pdf | Real Time Clock IC
U21 | IP5189T | QFN-24-1EP_4x4mm_P0.5mm_EP2.6x2.6mm | 1 |  |  | http://www.injoinic.com/wwwroot/uploads/files/20200220/3642884e4c0184d6c0173a5193cd56ce.pdf
U7 | LM324 | TSSOP-14_4.4x5mm_P0.65mm | 1 | LM324APT | 0.45 | https://eu.mouser.com/datasheet/2/389/cd00001046-1795623.pdf | TSSOP-14
U20 | MCP4822 | SOIC-8_3.9x4.9mm_P1.27mm | 1 |  |  | http://ww1.microchip.com/downloads/en/DeviceDoc/20002249B.pdf | 2-Channel 12-Bit D/A Converters with SPI Interface and Internal Reference (2.048V)
U14 U18 | MCP6S21 | SOIC-8_3.9x4.9mm_P1.27mm | 2 | MCP6S21-I/SN |  | https://www.rzxpoweric.com/data/upload/image/20210221/1613876184209693.pdf | High-Efficiency, 2A, 4.5V-21V, 500kHz Synchronous, Step-Down Converter, SOT-23-6
U17 | MT1470 | SOT-23-6 | 1 |  |  | https://www.rzxpoweric.com/data/upload/image/20210221/1613876184209693.pdf
U3 | PIC24EP256GP204 | TQFP-44_10x10mm_P0.8mm | 1 | PIC24EP256GP204-I/PT | 3.35 | https://eu.mouser.com/datasheet/2/268/70000657H-277982.pdf | 24bit Microcontroller
U16 | SP0503BAHT | SOT-143 | 1 | SP0503BAHTG | 0.8 | https://eu.mouser.com/datasheet/2/240/Littelfuse_TVS_Diode_Array_SP05_Datasheet.pdf-777043.pdf | SOT-143
U9 U10 U11 U13 | TL082 | SOIC-8_3.9x4.9mm_P1.27mm | 4 | TL082CDR | 0.41 | http://www.ti.com/general/docs/suppproductinfo.tsp?distId=26 | SOIC 8
X1 | 12MHz | Crystal_SMD_5032-2Pin_5.0x3.2mm | 1 |  |  | ~ | Two pin crystal
X2 | 32.768 kHz | Crystal_SMD_3215-2Pin_3.2x1.5mm | 1 | ABS07-166-32.768KHZ-T | 0.66 | https://eu.mouser.com/datasheet/2/3/ABS07-166-32.768kHz-T-1359238.pdf | RTC Crystal 32.768 kHz

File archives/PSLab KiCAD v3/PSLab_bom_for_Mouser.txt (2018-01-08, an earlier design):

Designator,MPN/Seeed SKU,Qty
"C1,C2,C4,C5,C9,C13,C17,C22,C24,C25,C26,C27,C28,C31,C32,C34,C35,C37,C38,C39,C41",0805YC104KAT4A,21
"C11,C14,C16,C18",TAJC107K016RNJ,4
"C12,C19",F971C336MBAHT3,2
"C7,C40",08055A103JAT2A,2
"C15,C21,C6,C33",TMK212BBJ106MG-T,4
"C8,C10",C0805C150K5RACAUTO,2
"C30,C36",08053F102K4T2A,2
"C20,C42",EMK212B7105MGHTR,2
"C23,C29",08053A3R3CAT2A,2
CON1,ZX62D-B-5P8(30),1
"D1,D2",BZV55C6V8,2
D3,HSMC-C170-T0000,1
D4,APHCM2012SYCK-F01,1
F1,SF-1206FP050-2,1
"J8,J6",640456-3,2
"J4,J10,J11,J12",640456-2,4
J5,640456-4,1
L1,KLZ2012MHR100HTD25,1
"P1,P10",M20-7820842,2
P3,M20-7821046,1
P5,M20-7820646,1
"Q1,Q3",MMBT3906LT3G,2
Q2,MMBT3904-7-F,1
"R1,R2,R3,R10,R14,R16,R17,R18,R19,R21,R22,R23,R25,R28,R29,R31,R32,R33,R35,R37,R38,R39,R42",RC0805FR-0710KL,23
"R4,R13,R54,R55,R56,R57",CRCW080518R0FKEA,6
"R5,R11,R27,R36,R47",RC0805JR-071KL,5
"R24,R34,R45",RCS08051M00JNEA,3
"R6,R7,R8,R9",ESR10EZPJ201,4
"R20,R30,R40,R46",KTR10EZPF2003,4
R49,CRCW0805560RJNEB,1
"R12,R15,R26,R41,R43,R44,R52,R53",RT0805DRD075K1L,8
RV1,RK09K11100E9,1
"U11,U12",MCP6S21T-I/MS,2
U2,MC74HC126ADR2G,1
U5,TC7660SEOA713,1
U6,ZLDO1117QG33TA,1
U7,LM324DT,1
U1,MCP2200-I/SS,1
U9,MCP4728-E/UN,1
U3,PIC24EP64GP204-I/PT,1
U4,TC1240AECHTR,1
"U8,U10,U13,U16",TL082CD,4
X1,LFXTAL003215Bulk,1

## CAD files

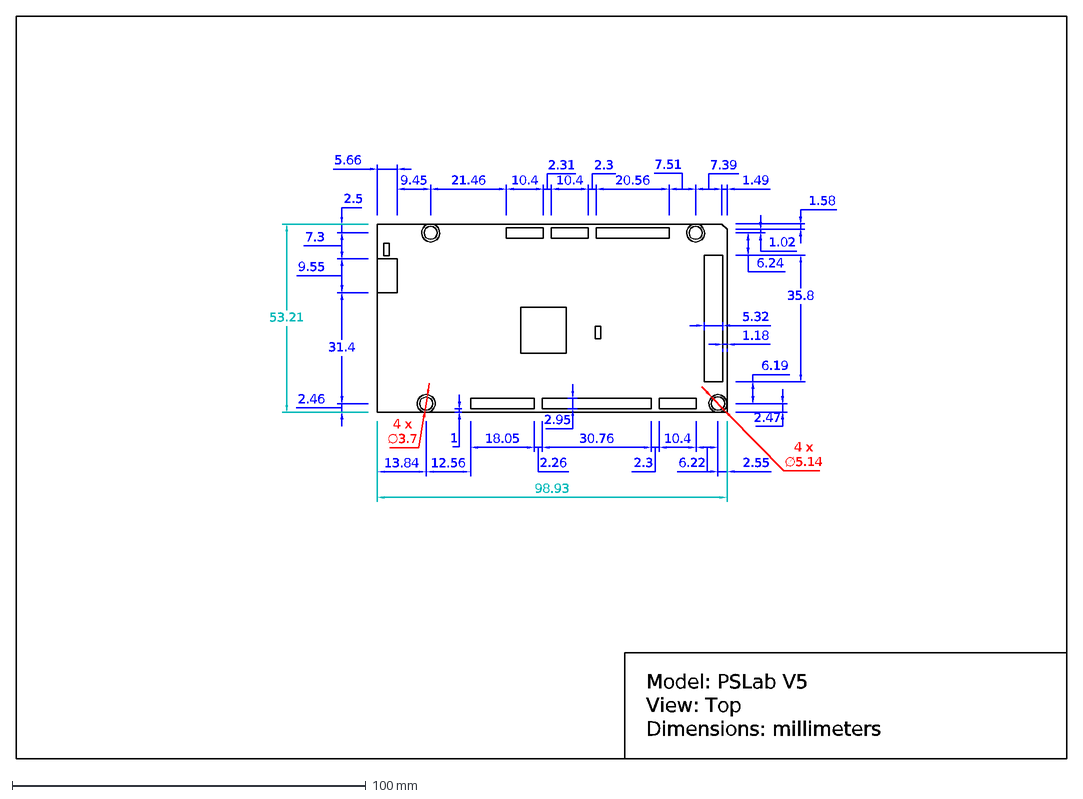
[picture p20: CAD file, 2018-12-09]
docs/drawings/PSLabUpper.dxf
2.47
6.19
35.8
6.24
1.02
1.58
1.49
7.39
7.51
20.56
2.3
10.4
2.31
21.46
9.45
2.55
6.22
30.76
2.26
18.05
12.56
13.84
1
5.32
2.95
2.5
7.3
9.55
31.4
2.46
5.66
4 x ∅3.7
4 x ∅5.14
53.21
98.93
1.18
Model: PSLab V5 View: Top Dimensions: millimeters

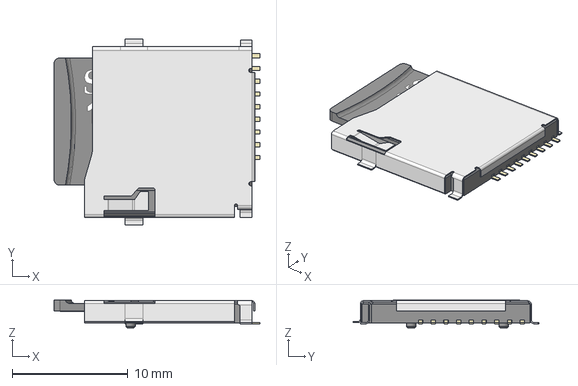
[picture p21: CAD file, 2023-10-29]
schematics/3DModels/TF-01A.step
17.8 x 16.1 x 2.40 mm

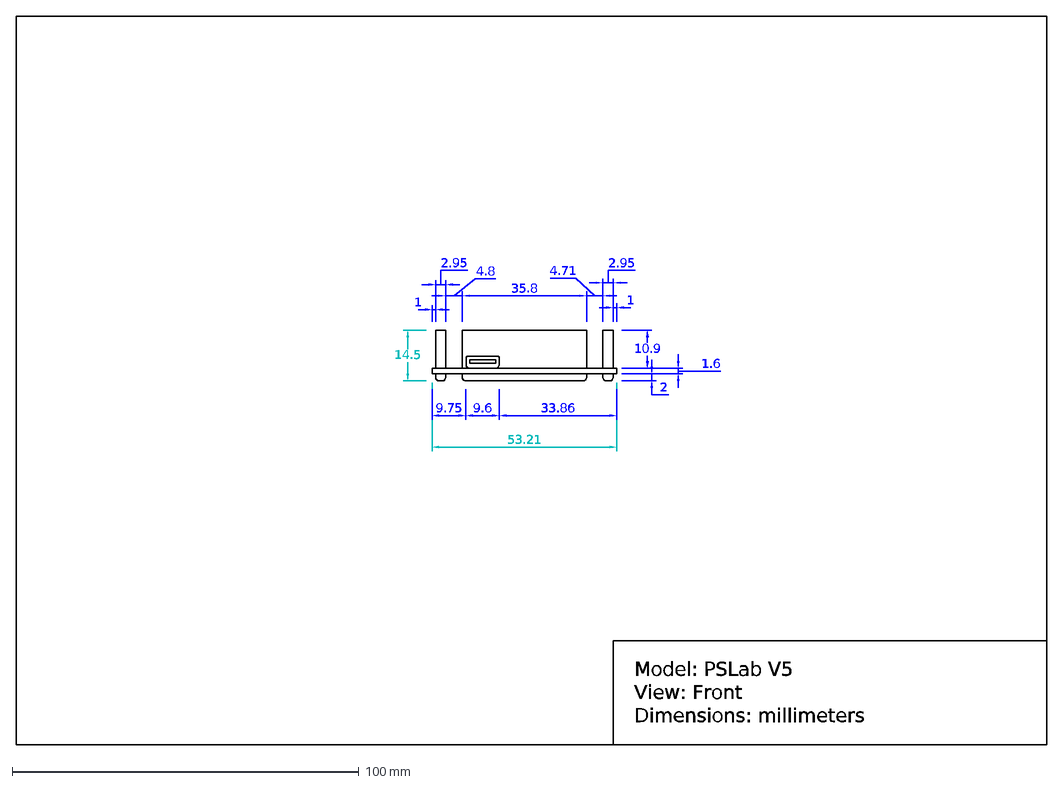
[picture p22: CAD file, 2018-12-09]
docs/drawings/PSLabFront.dxf
14.5
53.21
35.8
4.71
2.95
1
4.8
9.75
9.6
33.86
10.9
1.6
2
Model: PSLab V5 View: Front Dimensions: millimeters

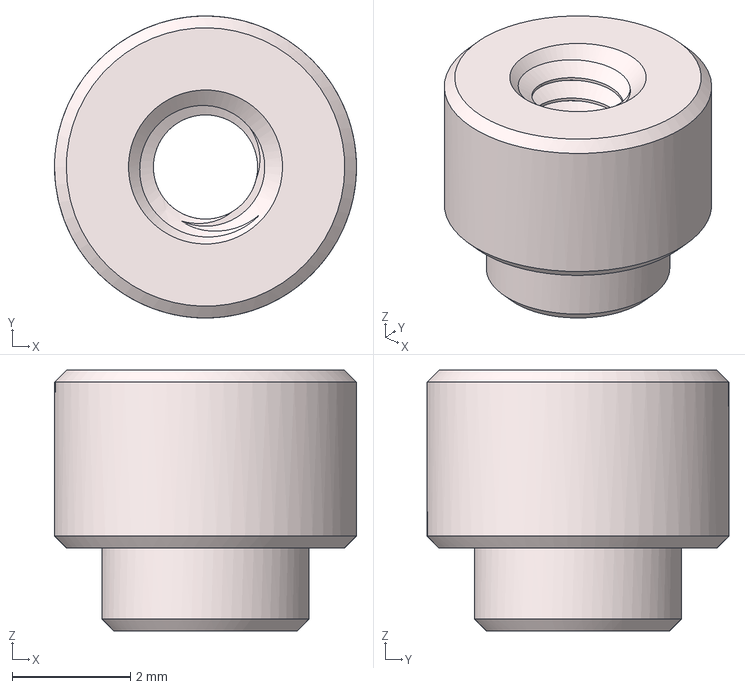
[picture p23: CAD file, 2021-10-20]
schematics/3DModels/Spacer.stp
5.10 x 5.10 x 4.40 mm

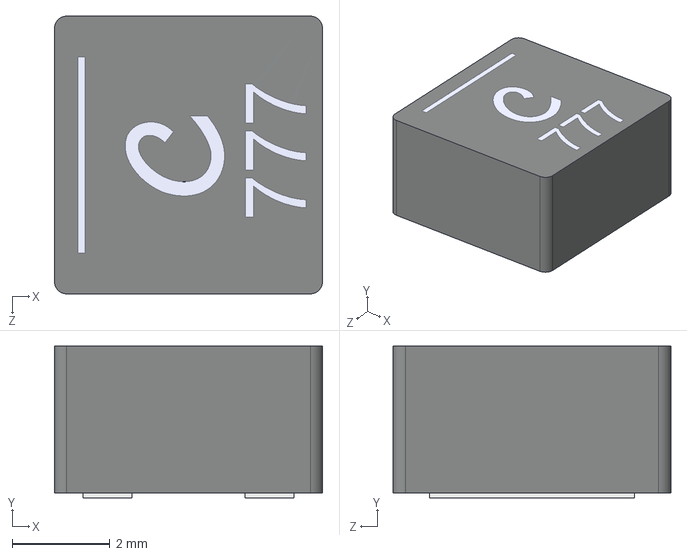
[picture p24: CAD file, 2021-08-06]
schematics/3DModels/Coilcraft-XAL5030.step
5.48 x 3.10 x 5.68 mm

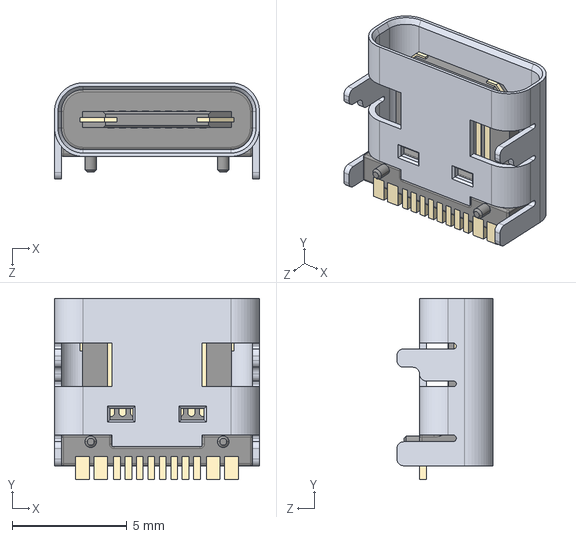
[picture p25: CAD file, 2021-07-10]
schematics/3DModels/USBCPort.STEP
8.94 x 7.90 x 4.20 mm

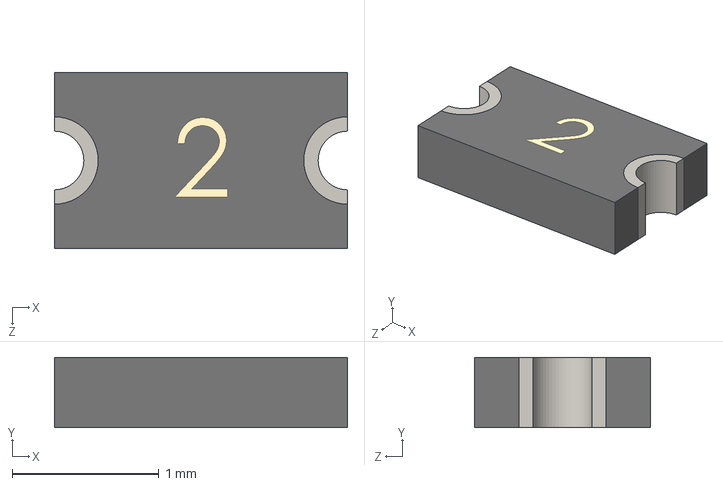
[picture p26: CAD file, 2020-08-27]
schematics/3DModels/Fuse.STEP
2.00 x 0.481 x 1.20 mm

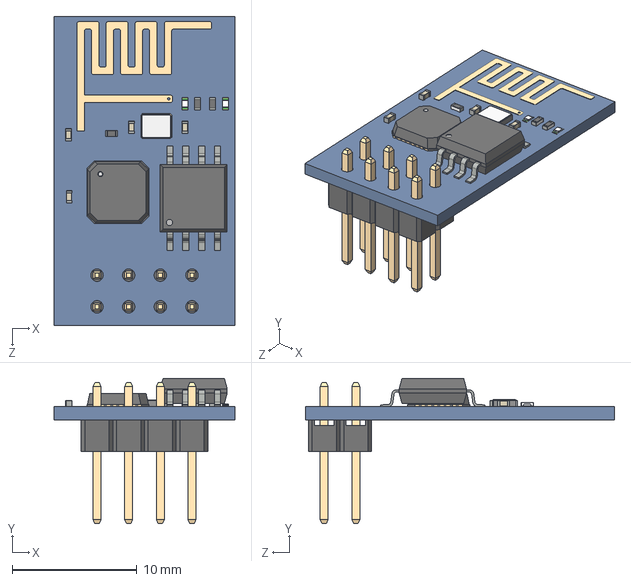
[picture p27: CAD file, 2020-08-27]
schematics/3DModels/ESP01.STEP
14.5 x 11.7 x 24.8 mm

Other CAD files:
docs/drawings/PSLabFront.dwg
docs/drawings/PSLabUpper.dwg

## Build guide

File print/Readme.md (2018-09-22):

This folders holds images that are printed on the front or back of the device.

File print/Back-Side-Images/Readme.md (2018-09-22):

The files in this folder are for the silk print on the backside of PSLab.

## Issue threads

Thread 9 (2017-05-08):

fossasia/pslab-hardware #9: Foot print components misaligned!

CloudyPadmal, 2017-05-08:
I checked the foot print of the PCB and it looks like this to me! Is it same for others?

[image]

jithinbp, 2017-05-08:
That's exactly how it looks to me. Not finished routing.
We need to make some hardware changes, so I'll have to spread out the
components and reroute.

- Add a Transistor+Zener based regulator for +/- power supplies instead of
the current resistor+zener regulator which is not efficient
- Move the I2C connector away from the CPU & give its Vcc pin some heavy
decoupling. This is because some I2C modules have tantalum capacitors for
decoupling. Ta capacitors have very low ESR and the Vcc of the chip itself
drops very quickly when they are plugged in.
- Instead of connecting Vcc of the I2C connector to 3.3V , we can consider
connecting it to 5V instead. I've found that more sensor modules have
connections like 5V GND SCL SDA instead of 3.3V GND SCL SDA even though
most work with 3.3V also since LDO regulators are used by them

- Replace 12MHz through hole crystal with 4-pin SMD crystals.

Are you well versed in KiCAD?

Also : Have the layout libraries properly been included in the git
repository? Schematic libraries had to be added later because they were
referencing a local folder on my PC.

thanks

CloudyPadmal, 2017-05-08:
Hey @jithinbp !! I haven't used KiCAD before but I went through their documentation yesterday! I've only worked with OrCAD and Proteus! :blush: 

There is a warning coming saying;
[image]

jithinbp, 2017-05-08:
I thought sudheesh had checked it after I added the library files. You might have to add the library  in the repo to KiCAD's path variable

CloudyPadmal, 2017-05-08:
Should I add it in this repo?

jithinbp, 2017-05-08:
I'm a little confused here.    Did you mean you will add the library? It's already there : proto1.lib
You can add it to the path variable, and if everything looks good, I'll pull the same

CloudyPadmal, 2017-05-08:
Ah yea! :D I added it to my kicad library path and now it's all fine :D :+1:

jithinbp, 2017-05-08:
cool! Maybe you can starting making sense of how it works.
Most of the schematic should be easy to understand. 

The NRF module is a major hassle during production. I hadn't planned on keeping it as part of this schematic, but in case we decide to use it, I think it might be easier to use the [SMD modules](https://www.aliexpress.com/item/5pcs-Free-Shipping-NRF24l01-2-4GHz-Wireless-Module-Mini-Version/32430542898.html) . Or, use the IC itself, and make the relevant circuitry including a PCB trace antenna. The 16MHz clock required for its operation can be derived from the PIC24 itself.

thoughts?

closed 2017-05-08 by jithinbp

CloudyPadmal, 2017-05-08:
Embedding the IC onto the current schematic would be better right? That module is like 2cm x 1cm but if we can implement it on the board itself with clock also derived from PIC, the space will be preserved I think! For the antenna we can even provide an IPX connector and an antenna right? :blush:

jithinbp, 2017-05-08:
The IC would be ideal, but it would be quite the cost addition. Two different versions can also be produced. Also, from what I've heard, the original IC from Nordic Semiconductors costs about $10 as opposed to the $1 chinese knock-offs that copied the silicon die itself to some extent along with the communication protocol. So we'll be going into production using knock-off chips. 
If the module is used, users can simply solder it on if they need it. Similar to the space provided for the ESP8266.
They can also choose to install a module with a built-in PA+LNA & rubber ducky antenna if they require longer range. modules are a flexible option.

CloudyPadmal, 2017-05-09:
If a space is left for user to solder a module himself, then we can simply implement the interface for the module right? Or is it a not so nice practice to provide just the female headers for connectivity of a module with male pins?
[NRF24L01](http://www.ebay.com/itm/1pcs-NRF24L01-2-4GHz-Antenna-Wireless-Transceiver-Module-NEW-C-/141975887566?hash=item210e6c1ece:g:gUQAAOSwLa9UXJmy)

That way, lot of space can be spared right?

CloudyPadmal, 2017-05-10:
Hello @jithinbp !!
Can I try to replace the TH crystal with an SMD crystal? :)

jithinbp, 2017-05-11:
Certainly. Can you try it in a separate layout file?
The crystal's schematic already exists in proto1.lib . It's a passive crystal with diagonally opposite terminals.  The other diagonal is grounded

You can also check out [Fox 924b](https://www.digikey.com/product-detail/en/fox-electronics/FOX924B-25.000/631-1074-1-ND/1024779) . It needs Vcc, GND , and outputs a highly accurate (+/-2.5ppm) 25MHz clock. Only two or three lines in the firmware will need to be changed for this hardware revision

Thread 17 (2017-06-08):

fossasia/pslab-hardware #17: Modify schematic library proto1.lib to comply with KiCAD's library testing utility

jithinbp, 2017-06-08:
PSLab KiCAD/proto1.lib does not currently pass the automatic schematic library testing utility provided by KiCAD.
The following procedure can be followed to check the errors
```
git clone https://github.com/KiCad/kicad-library-utils 
sudo kicad-library-utils/schlib/checklib.py <path to PSLab\ KiCAD>/proto1.lib 
```

at present, violations of the following nature are shown by the checklib.py utility
```
Checking symbol 'myUSBMB':
  Violating Rule 4.10 - Part metadata
  Violating Rule 4.12 - Footprint filters
  Violating Rule 4.2 - Symbol visual style
  Violating Rule 4.5 - Pin orientation
  Violating Rule 4.9 - Default fields
Checking symbol 'tp':
  Violating Rule 4.1 - Pin placement
  Violating Rule 4.10 - Part metadata
  Violating Rule 4.12 - Footprint filters
  Violating Rule 4.8 - Field text size
  Violating Rule 4.9 - Default fields
```

jithinbp, 2017-06-08:
A pretty amazing blog post of what can be achieved using travis can be found [here](http://scottbezek.blogspot.in/2016/04/automated-kicad-openscad-rendering.html)
It explains how travisCI can be used to automatically generate and display the CAD rendering in the README doc

jithinbp, 2017-06-08:
an automatic render of the schematic can also be made. [tutorial](https://scottbezek.blogspot.in/2016/?m=0)

CloudyPadmal, 2017-06-08:
We'll have to follow a similar procedure in `KiCAD` right since it is a CAD tool? :)

jithinbp, 2017-06-08:
First goal is to get the libraries to be accepted by the automatic script, otherwise we will keep getting build errors with Travis.
I am unable to find the rule list, and how to correct them. using trial and error. e.g. , `  Violating Rule 4.1 - Pin placement` is not verbose enough. The schematic works fine with KiCAD, but is somehow not accepted by the checking utility. Please share the rule list if you find one. I have found a few Travis logs for failed builds from other projects, and am locating sources for the builds that passed , so that I can compare the same with our library.

The blog posts I had linked to can be stretch goals. It uses Travis to generate and upload the latest render to a cloud link, and the same is embedded in the README.md

CloudyPadmal, 2017-06-09:
Sure! I'll share if a rule list is found! :+1:

CloudyPadmal, 2018-02-08:
Travis build is now passing with `library-check.sh` of KiCAD utilities repo, this issue can be closed!

closed 2018-02-08 by CloudyPadmal

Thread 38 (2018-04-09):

fossasia/pslab-hardware #38: Sell ready-made PCBs?

shakram02, 2018-04-09:
Hello,

I'm interested in having PSLab hardware. But I don't know the steps to fabricate one, since SMT assembly isn't available in my country.

Are you willing to sell ready-made PSLab kits through your website?

If no,
I've found [PCB cart](https://www.pcbcart.com/assembly) to make some copies. I don't know which format they accept.

It would be nice if you package the files in an amateur-friendly `zip` file with the instructions and your preferred PCB manufacturer if possible

Thank you

CloudyPadmal, 2018-04-14:
Hello @shakram02 ! The gerber files to manufacture the PCBs can be found [here](https://github.com/fossasia/pslab-hardware/blob/master/PSLab%20KiCAD%20v4/Gerber_For_PSLab.zip) and the bill of materials also can be found in [here](https://github.com/fossasia/pslab-hardware/blob/master/PSLab%20KiCAD%20v4/PSLab_bom_for_Mouser.txt)
For manufacturing you can go with any manufacturer you prefer!
Thanks!

shakram02, 2018-04-14:
Thank you @CloudyPadmal,

I recommend that you have an online store or sell it via a vendor, as you know PCB manufacturers only accept batch orders. I'm a student and won't be able to pay for 10 pcs to use only one. You can also get profit if you sell it online.

Thank you :+1:

shakram02, 2018-04-17:
look :sob: 
This is the cost from a manufacturer. I uploaded the files you mentioned. I need to buy  and 10PCS so the total is $908

[image]

CloudyPadmal, 2018-04-17:
Yes @shakram02 , I get the point! :disappointed: The quotation must be for a 2 layer board but PSLab is a 4 layer board; making the $5.59 upto $50 may be. Let's see if we can get you a device! cc : @mariobehling

shakram02, 2018-04-18:
@CloudyPadmal @mariobehling I'd love PSLab to be available for everyone also and not just me to get a device, maybe you can contact spark fun/ adafruit to sell them for you and get you a profit margin?

The reason is; In my university we have measurement devices from the 70s, and each 10 students stand around one device. That's extremely miserable and not fun at all, by making PSLab streamlined anyone can buy the kit easily and for the suitable price, while making you some profit.

Thank you :+1:

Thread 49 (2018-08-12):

fossasia/pslab-hardware #49: Considerations for Hardware Production Version 2018

mariobehling, 2018-08-12:
Below are considerations for hardware production from email exchanges with our partner at the Fraunhofer Institute and PCB manufacturer.

> The BOM allows to extract these information as well in manual fashion, however, most CAD tools will provide this info alongside the above mentioned pick and place information in one machine-readable file. So, if you verify the capabilities of KiCAD on the former, please check also on the latter requriements.
If KiCad is not able to do so, well, then back to manual :), same goes with the keep-out areas underneath the PCB for positioning of support pins during the printing process. With a "nest" (see below), this will not be needed.

> As to the PCB itself - could you check with your PCB supplier whether he could put the PCBs in a manufacturing panel ready for singulation either by milling, rolling blade separator (e.g. https://www.cab.de/de/elektronik/nutzentrenner/maestro-2-2m/) or hook knife (e.g. https://www.cab.de/de/elektronik/nutzentrenner/stegtrenner-hektor-2/). Milling will get the best contour precision (this is what you have now, but with separation prior assembly), the others will leave some minor jagged edges.
If the vendor is happy to panelize this for you, I would suggest a minimum 2x2, but for the sake for flexibility and speed preferrably a 3x6 (or any other option up to 460x460mm, suitable for print, assembly and soldering).
Here now the additional request - for the panels, we would need alignment marks, circles with min. 1mm/max 3mm diameter, exposed from any solder resist, to have the cameras identify the "copper pad positions" and then place the components into their final position. Without any alignment marks, the assembly system is "blind". This -in consequence- means if say we need to work on the singulated PCB, not only the total assembly time will go up, but also a dedicated nest with alignment marks would need to be built, the singulated PCB positioned relatively precisely into that nest, thus making the PCB ready for full-auto assembly. Can also be done, but is less elegant and "manufacturing like", compared to a panelization service by the PCB vendor :)

> For panelization, please note in the discussion with the vendor these additional needs
> - free area on the two "long" sides to allow for PCB-panel clamping: min3, preferred 5mm each side
> - preferred surface finish is NiPdAu ("enepig"), NiAu, tin (Sn) or Ag (most expensive!!). Also OSP can be used BUT note that any lower side population or repair will then be more critical due to the oxidation.
Please ask you vendor for a sample PCB to assess the solderability with the paste/reflow combination.

> Now to an additional (future adressing) aspects.
It seems that the core elements could be "squeezed" into modules, which can be modified if a new generation of µC or DAC appears. This will forego the need to design the whole PCB anew for the new generation, as it all can be handled on the module. Also, these modules can be significantly shrunk, if miniaturization needs arises in the future. You may want to consider this thought in a design revision of the future.

mariobehling, 2018-08-12:
PCB manufacturer feedback:

1. Output of coordinates of component central location
KiCAD generates pos files with centroid informations. The file content will look something like this;
2. BoM with both part details and assembly information
KiCAD doesn’t support a combined feature. We’ll have to do this manually.
3. Keepout areas underneath the PCB for positioning of support pins
“Same goes with the keep-out areas underneath the PCB for positioning of support pins during the printing process. With a "nest" (see below), this will not be needed.”
Design doesn’t have any components on the bottom side. So do we need any keep-out area for placement? I’m a little unclear about the “nest” as there was nothing attached below.
4. PCBs in a manufacturing panel
I checked with PCBWay and they provide a panelizing feature. We can make a panel and submit or ask them to create a panel for us.
They provide V-Scoring and/or Tab-Routing as the routing to separate boards.
5. Alignment marks on PCBs
Fiducial marks can be added to the existing design. I suppose a similar implementation like in the figure will do it, the alignments :)

6. Panelization specifications
- Free area on the two "long" sides to allow for PCB-panel clamping: min3, preferred 5mm each side
Possible
- Preferred surface finish is NiPdAu ("enepig"), NiAu, tin (Sn) or Ag (most expensive!!). Also OSP can be used BUT note that any lower side population or repair will then be more critical due to the oxidation.
PCBWay offers [HASL with lead], [HASL lead free], [ENIG], [Immersion gold], [OSP] and [Hard Gold]

mariobehling, 2018-08-12:
Reply from Fraunhofer:

This is very good news!

As no double sided assembly is required, we are free to position the support pins anywhere. Thanks for having clarified this. Also, with the option to go for the panel, no milled Al-nest (i.e. a negative form to receive the PCB to run it through the assembly line) is required.

As to the depanelization – what would be your preference (keeping your final form for sales in mind) -> V-groove may be cheaper but has some more rough edges, tab-routing will call for slightly larger inter-PCB distances (as of IPC 7351), but result in much cleaner edges. If you plan to mount the boards for your final product in a housing anyway, you may want to consider the price difference to your benefit!

Also on the cost side goes the PCB finish. We strongly discourage from HASL (lead) -> will bring you in trouble when running the RoHS and WEEE compliance check. With the current component sizes you have, HASL (leadfree) will still be acceptable w.r.t. pad surface flatness – as soon as you  go towards smaller components, this will eventually lead to assembly defects. ENIG w/immersion gold is currently the standard for volume production of hi-rel goods, so this is definitely to consider. Also OSP will be okay if the OSP chemistry provided by your PCB manufacturer can withstand minimum 2 thermal processes (1x full reflow, 1x soldering of the pins for the through hole components) – usually this should not be a problem, but I suggest to ask for a positive feedback to avoid issues later on. Immersion gold over copper (if I got this info right) is not a good choice, as diffusion is fast and will make the surface critcial to solder, especially if some storage time (ie. Producing first 100, then another 100, then 200 and 500  products) will deteriorate solderability. I strongly discourage the use of hard gold (plated), as –while initial soldering looks excellent- the overall reliability will be poor, making you a bad example of planned obsolescence in less than 2 years after manufacturing J

Alignment mark position and dimensioning is very good, thanks!

So, the next steps would be to exchange on the modified design with the alignment marks, receive the panel design file (stencil will be created for this entire size), freeze all designs, start buying components and PCB and go to us for the first full auto manufacturing run!

mariobehling, 2018-08-12:
Question of Padmal:

Once we make a panel, say 3 x 2 boards in one panel. For the automated pick and place machine, should we provide component coordinates to all the components on the panel or providing coordinates to only one board is enough? (Will it offset coordinates to other components of the same ID?)

cweitat, 2018-08-12:
@woshikie do have a look at this as well.

CloudyPadmal, 2018-08-13:
Reply from Fraunhofer:

One additional point to my previous answer.... For the Stencil, the full panel info on the opening site is preferred, saves us some days for measurement, panelling of stencil coordinates and ordering...

CloudyPadmal, 2018-08-13:
Padmal:

With KiCAD we can generate positions of the same component in multiple places. If we prepare the stencil matching that I guess we can straightaway configure the pick and place machine to assemble the whole panel at once :)

[image]

PR #114 (2020-08-27): fix: upgrading hardware design
This pull request is addressing all the issues left in [Milestone 1](https://github.com/fossasia/pslab-hardware/milestone/1)

1. fix #104 : removed crosshair (drill origin map) 
[image]
2. fix #97 : increased cutoff frequency using 0.5pF capacitor replacing 3.3pF
3. fix #105 : USB type C with 12 pins
4. Added UART reset connector for ESP, Bluetooth and USB connections
5. fix #75 : External power supply support
6. UART support on dual ports. (Possible to use two UART connections simultaneously)
7. fix #106 : I2C pins inline with OLED screens (VCC/GND swapped to su [... cut]
closed 2020-08-27 by CloudyPadmal

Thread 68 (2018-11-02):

fossasia/pslab-hardware #68: two layer version for reduced costs

shakram02, 2018-11-02:
Is it possible to make pslab available in a two-layer version? having 4 layers makes PCB fabrication pretty expensive. 

Maybe you can increase the area for it to be like a tablet if needed, in my opinion, it's more important that the circuit becomes cheap and easy to fabricate than to keep it small in size

Thanks

CloudyPadmal, 2018-11-03:
Hello @shakram02 ! It could be possible to make a two layer board with expanded area. But this will require tremendous amount of time and effort to balance loads and signal tracks and it will have some other issues as well;

1. Current design dimensions are roughly around 100mm x 50mm. If we take a 2 layer board into account assuming that we are making 5 boards, this would cost about $5 and if we increase one millimeter from width making it 101mm x 50mm, the new cost will be $30 for 5 boards. (Yes of course we can increase 50mm side but will we be able to stay inside the 100mm x 100mm area is a question)

2. Bigger the circuit, bigger the interference to signals as they are traversing a longer distance. Especially to the tracks connecting sensitive instruments such as oscilloscope circuitry.

4. When the mass production is happening, the cost difference between 2 layer and 4 layer is bearable and it will actually save some money when it comes to shipping as the weight of the board is lighter in smaller 4 layer boards.

5. It won't be "Pocket" Science Lab anymore :)

#### And I got good news. The new stocks are ready and they will be available to order online pretty soon. I will ping you here when the ordering is ready for your convenience. It will be just a few more dollars than a regular Arduino Mega board :)

shakram02, 2018-11-03:
`
And I got good news. The new stocks are ready and they will be available to order online pretty soon. I will ping you here when the ordering is ready for your convenience. It will be just a few more dollars than a regular Arduino Mega board :)
`
That's super cooool :boom:

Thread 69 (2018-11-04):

### ISSUE TITLE
Rethink usage of Tantalum capacitors

### ISSUE THREAD

**Issue by gallioleo** [fossasia/pslab-hardware#69]
From the ethical point of view are tantalum capacitors critical, cause tantalum is a conflict mineral - see link below. Another point are the cost of this capacitor. If the project doesn't need the high capacitance with small geometrical size, you should think about the phase out of these caps.

https://www.electronicdesign.com/blog/conflict-minerals-and-tantalum-capacitor-supply-chain

**Comment by cweitat** [comment]
@gallioleo according to KiCad, we are using KEMET but we are using Samsung capacitors during production. So not much problems with that. We will still take your view into consideration. Thanks :)

http://images.samsung.com/is/content/samsung/p5/pl/aboutsamsung/2017/pdf/About-us-sustainability-report-and-policy-confilct-mineral-policy-en.pdf

http://www.samsungsem.com/global/product/passive-component/tantalum1/index.jsp

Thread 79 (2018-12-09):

fossasia/pslab-hardware #79: PSLab Hardware V2 - new chips

mariobehling, 2018-12-09:
There are better chips available for future versions of PSLab. One recommendation is LPC43S70FET256: 32-bit ARM Cortex-M4 + 2 x M0 MCU; 282 kB SRAM; Ethernet; two HS USBs; 80 Msps 12-bit ADC; configurable peripherals, AES engine

https://www.nxp.com/products/processors-and-microcontrollers/arm-based-processors-and-mcus/lpc-cortex-m-mcus/lpc4300-cortex-m4-m0/32-bit-arm-cortex-m4-plus-2-x-m0-mcu-282-kb-sram-ethernet-two-hs-usbs-80-msps-12-bit-adc-configurable-peripherals-aes-engine:LPC43S70FET256

Because of the on board 80 MSPS ADC, 6 channel and so the oscilloscope function would be able to capture faster signals and 12 bit accuracy should be sufficient enough for most uses.

cweitat, 2018-12-23:
Alternatively, to look at FPGA for better specifications

geekyjoyce72, 2018-12-23:
> Alternatively, to look at FPGA for better specifications

Hmmm but still, performance in terms of analog and digital sampling/signal generation is really down to the AD/DA converters and their specs. FPGA will drive the cost and design complexity up needlessly, compared to a MCU like the one suggested.

I don't see an application here that justifies the use for FPGA. Thoughts?

cweitat, 2018-12-23:
@geekyjoyce72 is just an alternative that we can KIV. :)

geekyjoyce72, 2019-03-01:
https://www.nxp.com/products/processors-and-microcontrollers/arm-based-processors-and-mcus/lpc-cortex-m-mcus/lpc4300-cortex-m4-m0/32-bit-arm-cortex-m4-plus-2-x-m0-mcu-282-kb-sram-ethernet-two-hs-usbs-80-msps-12-bit-adc-configurable-peripherals:LPC4370FET100

Actually, there's also a 100 pin version, this will make routing easier to handle. 

I honestly am thinking about building one of these boards with the LPC MCU myself first, what do you think?

mariobehling, 2019-03-01:
Nice! Please go ahead and post a basic design in a new folder in this repo.

orangecms, 2020-11-29:
I am currently looking at a handful of development boards that I recently got to see what platforms are nice to develop on.

AT SAM D MCUs and other AT SAM MCUs are probably sufficient to bring all the features we need to switch platforms.
I have a [XIAO board](https://www.seeedstudio.com/Seeeduino-XIAO-Arduino-Microcontroller-SAMD21-Cortex-M0+-p-4426.html), which is a SAM D21. I'm trying various environments, looking into [Zephyr](https://docs.zephyrproject.org/1.13.0/reference/kconfig/choice_24.html) and [FreeRTOS](https://github.com/BriscoeTech/Arduino-FreeRTOS-SAMD21), possibly [RIOT OS](https://github.com/RIOT-OS/RIOT/tree/master/cpu/samd21), [bare Rust](https://github.com/atsamd-rs/atsamd), and [Arduino](https://github.com/arduino/ArduinoCore-samd), the latter being quite complex regarding build setup for CI.

I am not exactly sure what is necessary in order to get the hardware features that the current PSLab has, so I am mostly looking from a software/firmware development perspective.

Here is a decent overview of the MCU market: https://jaycarlson.net/microcontrollers/

fcartegnie, 2021-01-18:
As dev boards STM32 discovery kits do provide STLink on board (dual USB) for free. old STMF1 are cheap.
STM32F1 series are too limited

The chinese DSO138 Kit using STM32F1 has 1Msps over 1 chan and provides LCD screen for 15$. There's no point of making a similar device for higher price and less hardware.

The PIC "secondary" 2Msps chip can still be driven by an STM to provide 4chans. (assuming we can have enough bw between the 2)

If we need to target a single chip, then we don't care about frequency. We must focus on RAM and ADC capabilities. Having a 72MHz chip that performs worse than PIC is useless, because the ADC Clock does not run at the MCU speed.

Ex: STMF3 provides DMA and RTC. There's far more chip versions. Should consider "ADC Clock" first.

https://hsel.co.uk/2015/12/10/stm32f0-high-sample-rate-adc-usage/
https://www.stmicroelectronics.com.cn/content/ccc/resource/training/technical/product_training/group0/3c/ee/54/92/43/f1/4e/27/STM32H7-Analog-ADC_ADC/files/STM32H7-Analog-ADC_ADC.pdf/_jcr_content/translations/en.STM32H7-Analog-ADC_ADC.pdf

fcartegnie, 2021-01-18:
Provides summary table with max SPS per chip
https://www.st.com/resource/en/application_note/dm00129215-extending-the-dac-performance-of-stm32-microcontrollers-stmicroelectronics.pdf

orangecms, 2021-01-20:
[image]

for quick comparison, here's the table from the DAC performance document

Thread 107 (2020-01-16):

fossasia/pslab-hardware #107: Move ESP to frontside

mariobehling, 2020-01-16:
The ESP chip is the only module on the backside of the device. Please try to decrease the usage of space on the board and move the chip to the front side.

CloudyPadmal, 2020-01-17:
ESP is about 1/10th of the whole board and even if we managed to bring it to the top, it would not go with the same solder flow as other components as it is a module. Need to evaluate the effort with the outcome we would get from this.

CloudyPadmal, 2020-02-26:
Current version in use is ESP12. Most of the pins in this module are unused in PSLab. With this reasoning, we can replace ESP12 with ESP01 which will enable us to move the component to top.
[image]

CloudyPadmal, 2020-05-18:
Added in #93

PR #113 (2020-05-18): feat: esp01 module
Fixes #107 

- Replaced current ESP12 module with ESP01 to bring it to the top side.
- Routing errors fixed

[image]
<table>
<tr>
<td>[image]</td>
<td>[image]</td>
</tr>
</table>
closed 2020-05-18 by CloudyPadmal

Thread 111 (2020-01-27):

fossasia/pslab-hardware #111: Wave Generator: Triangle wave is deformed

Low012, 2020-01-27:
When I configure the wave generator to output a triangle wave, the wave which is generated is deformed. I checked with the PSLab's oscilloscope and with an external device.

I would expect the wave to look like the wave that is displayed in the app. 

1623Hz triangel wave
[image]

[image]

615 Hz triangle wave
[image]

[image]

justinclift, 2020-01-28:
Ouch. :frowning_face:

19-pragya, 2020-08-15:
can i work on this??

marcnause, 2023-02-06:
I am pretty sure that this is a software issue in the Android app. I will close this issue and add a comment to https://github.com/fossasia/pslab-android/issues/2100 instead.

closed 2023-02-06 by marcnause

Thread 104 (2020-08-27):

### ISSUE TITLE
Crosshair in outline layer

### ISSUE THREAD

**Issue by kasbah** [fossasia/pslab-hardware#104]
Hey, it seems there is a crosshair drawn on the outline layer in the lower left side. Here visualized with the [tracespace viewer](https://tracespace.io/view).

![image](https://user-images.githubusercontent.com/206854/64679947-4888eb80-d46c-11e9-8458-a371f8fd3f27.png)

This causes the tracespace viewer not being able to render the board in the realistic mode at all. [On Kitspace](https://kitspace.org/boards/github.com/fossasia/pslab-hardware/) it looks like this:

![image](https://user-images.githubusercontent.com/206854/64680100-a3bade00-d46c-11e9-9811-3ae1447ff3db.png)

**Comment by CloudyPadmal** [comment]
Ah it looks like the origin marking from KiCAD. Let me make a fix :thinking:

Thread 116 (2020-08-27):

### ISSUE TITLE
Digital inputs are mislabeled on bottom 

### ISSUE THREAD

**Issue by bessman** [fossasia/pslab-hardware#116]
The digital inputs (LA1-4) are mirrored on the bottom of the board. The pin labeled LA1 is actually LA4, LA2 is LA3, LA3 is LA2, and LA4 is LA1.
![](https://i.imgur.com/3yMs9DO.jpg)
![](https://i.imgur.com/4ZMKe5i.jpg)

**Comment by CloudyPadmal** [comment]
This pin set has been removed in the new version to give space for RTC battery. So I guess we can close this issue.

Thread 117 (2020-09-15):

fossasia/pslab-hardware #117: Implement feature to turn off PSLab components to save power

mariobehling, 2020-09-15:
The question is if PSLab's components can be selectively turned off to save power? And what's PSLab's rough baseline power consumption? 

Bakcground:
> I'm really interested in developing a project to build OSH wildlife monitoring sensors and it would be amazing if it could be based on, or related to, PSLab. I know many ecologists and conservation biologists who would love access to technology like PSLab to adapt/remix but lack the expertise to do so.
> The key to autonomous sensing, though, is power supply, hence my questions above. Many of PSLab's existing components could be useful in a remote-sensing context, but ideally they should only be powered on when needed. For example, it would be cool if the wireless modules are turned on only when someone wants to establish a data connection in the field. I recall discussing power requirements at a hack-a-thon, and even a Raspberry Pi is way too power-hungry to work well...

penyuan, 2020-09-28:
Thanks for opening this issue!

As someone who has worked in the field, I'd be happy to elaborate more if/when needed.

RafaelLeeImg, 2023-09-20:
The next version v7 will use ARM chip and less power rail to save power.

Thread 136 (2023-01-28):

fossasia/pslab-hardware #136: Populate ICSP header

bessman, 2023-01-28:
### Problem Description

On the latest prototype, the ICSP header (which is used to flash the device with a hardware programmer) is unpopulated. While this header is not commonly used, populating the header makes it easier to e.g. replace the bootloader if necessary.

mariobehling, 2023-09-11:
The ICSP header is populated, but it could be that it was not soldered on the board. We will make a production note that the pins get soldered onto the device as well.

mariobehling, 2023-09-11:
@CloudyPadmal Could you tell us, please why the pin order is reversed relative to the previous prototype? What is the reason for that?

CloudyPadmal, 2023-09-15:
Is it compared to V4 where we have ICSP headers parallel to the board's lengthwise edge?

bessman, 2023-09-15:
Compared to the first V6 prototype. I think it also had the ICSP header perpendicular to the board's lengthwise edge, but the pin order was reversed.

I don't have the boards in front of me right now, and looking through the git history I can't actually find a point where the order was reversed. It's possible I'm mistaken. I will check tonight.

bessman, 2023-09-15:
edabd6f changes the orientation of the header. The pin order is the same then as it is now, so I guess I'm mistaken. Will double check with the actual board later.

bessman, 2023-09-15:
No, on the previous prototype the header is still parallel with the lengthwise edge. I don't know why I thought the order was reversed :thinking: Forget it.

Keeping this issue open for now to make sure we remember to have the header soldered on the production boards.

RafaelLeeImg, 2023-09-20:
Is ICSP headers soldered on PSLab v5? If yes, was it male or female?

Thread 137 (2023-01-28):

fossasia/pslab-hardware #137: Document new buttons and LEDs

bessman, 2023-01-28:
### Problem Description

The new prototype has several new buttons and LEDs. Some are self-explanatory (RESET), while others could use some documentation explaining their purpose.

In particular:

- The BOOT button. Through trial-and-error I found out that keeping BOOT pressed while resetting the device makes it boot into bootloader mode.
- What does the POWER button do?
- What is the purpose of the four white LEDs mentioned in #135?

mariobehling, 2023-09-11:
> The BOOT button. Through trial-and-error I found out that keeping BOOT pressed while resetting the device makes it boot into bootloader mode.

Correct.

> What does the POWER button do?

The user needs to press this button to activate the output of the power converter. It means if the user uses a battery they can use this button to switch on/off the device. Switch on: Press one time. To switch it off press two times within one second to shut down the device.

> What is the purpose of the four white LEDs

With all 4 lid up it means the battery is fully charged. 

To be tested: What happens when connected to USB?

bessman, 2023-09-11:
> To be tested: What happens when connected to USB?

When my prototype is connected to USB, three of the battery LEDs light up and the fourth blinks with a period of ~1 sec.

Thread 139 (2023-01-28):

fossasia/pslab-hardware #139: Power supply not working

bessman, 2023-01-28:
### Problem Description

The power supply pins (PCS, PV1, PV2, PV3) on the new prototype are not working. I recall we changed the chip driving the power supply, correct? Do we need to update the firmware to make the new driver chip work?

CloudyPadmal, 2023-02-11:
New IC: https://www.microchip.com/en-us/product/MCP4822

bessman, 2023-02-20:
The new prototype uses a muxer for the SPI chip select.

### Differences between hardware versions

#### V5

Three SPI chip select outputs:

1. The external CS pin on the SPI header, controlled by C4
2. The gain amplifier for oscilloscope channel 1, controlled by A10
3. The gain amplifier for oscilloscope channer 2, controlled by A7

#### Old prototype

Adds another chip select output for the SD card, controlled by B9.

#### New prototype

Adds another one, for the MCP4822 controlling the power supply. The v5 and the old prototype used a different chip which was connected via I2C.

This brings the total to five, for which we did not have enough free pins available. Thus the muxer.

The muxer is a TI CD74HC4051 Analog Multiplexer and Demultiplexer. It has three inputs and eight outputs. One output at a time can be set high by asserting the three inputs, according to the following table:

| S2 | S1 | S0 | OUT |
|---|---|---|---|
| L | L | L | A0 |
| L | L | H | A1 |
| L | H | L | A2 |
| L | H | H | A3 |
| H | L | L | A4 |
| H | L | H | A5 |
| H | H | L | A6 |
| H | H | H | A7 |

Additionally, all outputs can be set low by setting the E pin high. In the PSLab's case, the E pin is currently connected to ground, so one output will always be high.

The muxer is connected as follows:

Inputs:
A10 (previously CH1 gain) -> S0
A7 (previously CH2 gain) -> S1
B9 (previously SD card) -> S2

Outputs (AX refers to the muxer output pins here):
A0 -> CH1 gain
A1 -> CH2 gain
A2 -> Power supply
A3 -> NC
A4 -> External CS pin
A5 -> SD card
A6 -> NC
A7 -> NC

C4 (which previously controlled the external CS pin) is now NC.

### Way forward

If possible, the firmware should have an abstraction layer around the CS pins, such that setting a certain CS pin can be done in the same way regardless of which underlying pin controls that CS pin. A rudimentary abstraction layer currently exists in pin:manager.h, which maps MCU pin <-> CS pins 1:1. 

Investigate how this abstraction layer could be extended to decouple the CS pins from the MCU pins.

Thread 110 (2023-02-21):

### ISSUE TITLE
Collect data of different sensors / pins in parallel

### ISSUE THREAD

**Issue by mariobehling** [fossasia/pslab-hardware#110]
Would it be possible to collect data in parallel. E.g. the idea would be that the Android app configures several instruments and transfers the commands to the device to collect data from several pins.

**Comment by bessman** [comment]
This is possible as long as the pins do not use the same underlying hardware or firmware resource.

For example:

- the oscilloscope and logic analyzer cannot be used simultaneously because both store data in the same buffer (firmware limitation).
- The function generator pins (SI1 & SI2) cannot be used at the same time as PWM pins SQ3 and SQ4, because they are controlled by the same MCU pins (C8 & C9) (hardware limitation).

There are improvements that can be made in this area, but those improvements would go in either the firmware or the UI. Closing this as too broad and not hardware related.

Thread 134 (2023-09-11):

### ISSUE TITLE
RGB LED not working

### ISSUE THREAD

**Issue by bessman** [fossasia/pslab-hardware#134]
### Problem Description

On the latest prototype, the onboard WS2812B RGB LED does not work.

#### What steps reproduce the problem?

Power the device. The LED should light up, but does not.

#### What is the expected output?

The LED should light up when the PSLab is powered.

**Comment by mariobehling** [comment]
The WS2812B RGB LED has the option to generate any color. It is not only red. If it does not work it is an issue with your specific board.

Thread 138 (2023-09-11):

### ISSUE TITLE
SYSTEM / STATUS LED

### ISSUE THREAD

**Issue by bessman** [fossasia/pslab-hardware#138]
### Problem Description

On the new prototype, the LED previously labelled SYSTEM is renamed to STATUS. Why? It seems like an unnecessary change that will lead to confusion since old documentation will need to be updated to reflect the new name.

Its location has also been moved next to the backup battery slot. I think the old location next to the MCU is better, since the new location gives the impression that it's a status LED for the backup battery.

**Comment by mariobehling** [comment]
The name change was done by @CloudyPadmal. Could you explain why this was done, please?

@bessman The change of the location was done due to hardware changes. More space was required and the PIN layout had to be changed.

**Comment by bessman** [comment]
If I recall correctly, @RafaelLeeImg thought it would be possible to move the LED closer to the MCU.

But in any case, the position and name of this LED is a minor detail which should not take up significant time or attention. Since we're rather short-handed at the moment, I'm closing this so that it doesn't clog the backlog.

**Comment by CloudyPadmal** [comment]
If I recall correctly, the LED was renamed to `Status` as it shows the status of MCU operations.

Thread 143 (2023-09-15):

### ISSUE TITLE
Voltage measurement incorrect when powered via USB

### ISSUE THREAD

**Issue by everthu** [fossasia/pslab-hardware#143]
I've different measurement values for a voltage measurement with PSLab by the use of different  USB sources.
If I use a laptop to power the PSLab board, the voltage measurement is too low. While I should measure a voltage of 6v, the actual voltage measured by PSLab is 4.8v. 
When using a regular PC as USB source I'am measuring a correct voltage of 6v.
It seems like that the USB bus power in case of a labtop is low, around 4,5V.
I was assuming that the PSLab board is using internal reference sources to correct for this issue.
Does someone has any idea what is going on?
The used hardware is V5

**Comment by bessman** [comment]
4.5 V is below the required input voltage of the PSLab's voltage regulator (4.75 V). The analog inputs do have internal voltage refs, but if the supply voltage is too low they become inaccurate.

Basically, if the supply voltage is outside spec all bets are off. Nothing we can do about it.

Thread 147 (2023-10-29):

### ISSUE TITLE
Use kibot to generate diffs

### ISSUE THREAD

**Issue by CloudyPadmal** [fossasia/pslab-hardware#147]
Instead of terminal based diff images, now `kibot` has an option called 'diff' that generate diff pdfs between schematics and PCBs. (https://github.com/INTI-CMNB/KiBot)

We may use that for reviewing changes.

**Comment by CloudyPadmal** [comment]
~Fixes in #146~

**Comment by bessman** [comment]
Cool!

How does one read the diffs? At a glance, the diff_schematic.pdf looks identical to PSLab.pdf, just in black-and-white.

**Comment by CloudyPadmal** [comment]
Something is not right with the diff configuration in `CI.kibot.yaml`. The PDF should look like this: [diff_schematic.pdf](https://github.com/fossasia/pslab-hardware/files/13053734/diff_schematic.pdf) with red and green stuff

**Comment by CloudyPadmal** [comment]
Now it works! 🚀

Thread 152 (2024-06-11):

fossasia/pslab-hardware #152: Board Temperature

CloudyPadmal, 2024-06-11:
I just measured board temperature using in-built methods.

| Old Prototype Board - Old Firmware | Old Prototype Board - New Firmware | New Board - New Firmware |
| ---------------------------------- | ---------------------------------- | ----------------------------- |
| [image] | [image] | [image] |

New board MCU gets up-to 43 Celsius when the old prototype MCU is around 30-32 Celsius.

bessman, 2024-06-11:
I don't think this is a problem in and of itself; 43 °C is not worrisome in the sense that it might damage anything. But it does indicate greater power consumption.

This may be related to the resettable fuse problem, and means that battery life in stand-alone mode will be shorter than it could be.

bessman, 2024-06-11:
Any idea what might be causing it?

One thing that's different between the old and new prototype is the addition of the battery indicator LEDs. As noted elsewhere, they are VERY bright. I wonder if they could be the cause of the increases power draw? Would that manifest as greater MCU temperature?

CloudyPadmal, 2024-06-12:
I'm not sure what could be the cause. 

It looks like the RGB LED is mounted in reverse and may be it is drawing current. I plan to look more into this in this week.

CloudyPadmal, 2024-06-14:
I rotated the RGB LED and looks like now it does not heat up anymore.

[image]

However, the RGB LED does not light up. I'll try to solder a new one and see as they are quite plasticky and highly possible to get damaged due to reworking with hot air.

bessman, 2024-06-14:
I suppose this also explains why the RGB LED doesn't work on any of the recent prototypes.

mariobehling, 2024-06-14:
Is this wrong in the schematics?

bessman, 2024-06-14:
Looks correct to me:
[image]
[image]

I wonder how it ended up backwards? :thinking:

cweitat, 2024-06-14:
@bessman are u able to check the LED to see if it has the +- sides as the intended component? because sometimes the chinese made chips have reversed poles.

bessman, 2024-06-14:
Will check tonight unless @CloudyPadmal checks first.

cweitat, 2024-06-14:
One more thing to check. which colour of LED does it happened? White/Green/Blue

CloudyPadmal, 2024-06-14:
This notch in the LED should face towards the MCU. It was like that in the early prototype Rafael sent over to us.

| 3D render | Rafael Prototype |
| --------- | ---------------- |
| [image] | [image] |

But this is not the case with the new boards and somehow the LED is rotated. I just checked the `position` file and the rotation is 0 degrees as expected (D5 - Line 52).

Since this rotation causes the `VCC` and `GND` pins to swap, it might have fried the LED in the first place. Let me double check with a new WS2182B LED.

[image]

bessman, 2024-06-14:
> One more thing to check. which colour of LED does it happened? White/Green/Blue

It's the RGB LED. It can be any color. It should be purple in bootloader, green in application.

> @bessman are u able to check the LED to see if it has the +- sides as the intended component? because sometimes the chinese made chips have reversed poles.

It's the same as in the datasheet:
[image]

Previous prototype (correct orientation):
[image]

Current prototype (wrong orientation):
[image]

Comparison between previous and current prototypes with board traces marked in yellow and LED pins marked in red:
[image]
[image]

CloudyPadmal, 2024-06-14:
Looks like the model got protection against reverse connections.

[image]

cweitat, 2024-06-16:
What can we conclude from here? That the GERBER wasn't followed in regards to the LED direction and because of this, it resulted in faults of ____?

CloudyPadmal, 2024-06-16:
> What can we conclude from here? That the GERBER wasn't followed in regards to the LED direction and because of this, it resulted in faults of ____?

I will finalize this by tomorrow or the day after at the latest.

CloudyPadmal, 2024-06-17:
So I was able to test again.

The RGB LED was burnt and I replaced it with a spare one and now it lights up.

[image]

I did a temperature test, and it seems normal with the new RGB LED.
[image]

Now the conclusion is that, 

- The RGB LED (D5) requires manual de-soldering to correct its position.
- [`PositionFile.csv`](https://github.com/fossasia/pslab-hardware/blob/pslab-v6/docs/position_files/PositionFile.csv) is still correct. I'm not sure why the LED was rotated during assembly.
- I suspect that the fuse was protecting the board from this LED creating a short. Therefore, we will pause the fix we had earlier (shorting the fuse) until a fresh board is tested with the LED in the correct position.

cweitat, 2024-06-18:
I had a chat with the manufacturer side and they want to clarify few items:
[image]
does the yellow circle meant the direction of placement for the component?

More example of the schematics
[image]
[image]
[image]
[image]
[image]

CloudyPadmal, 2024-06-18:
The yellow circle marks the pin 1 in an IC or a component. Also on the silk screen, a special marking shows where a special marking of an IC or a component should align.

[image]

In this figure I have marked such markings for the MCU and the RGB LED.

CloudyPadmal, 2024-06-18:
The standard is that this special marking is next to pin 1. Apparently for WS2812B RGB LED, the special marking is next to pin 3. Maybe this is where it went off-road for the manufacturer.

[image]

CloudyPadmal, 2024-06-21:
## Conclusion

The recently manufactured and assembled boards have an issue.

The issue is that the RGB LED (WS2182B) (D5) is mounted incorrectly, with the VCC (pin 1) and GND (pin 3) swapped. This creates a type of short circuit, rendering the board unusable unless the LED is manually removed and repositioned correctly according to the parameters in the provided PositionFile.csv.

It appears that the manufacturer missed the visual inspection step to verify that the IC pin markings align with the silk screen markings. This issue was caused by the manufacturer’s fault, as all the specifications and files we provided were correct.

@mariobehling @cweitat

cweitat, 2024-06-21:
@CloudyPadmal only Gerber and BOM was given to the manufactuerer. Is the positionfile.csv in the gerber package?

CloudyPadmal, 2024-06-21:
@cweitat `Pick and Place` and `Position` are the same file, with different names.

cweitat, 2024-06-24:
Reply from them: Pick and Place procedure is not able to verify the direction of the components, only the positioning.

CloudyPadmal, 2024-06-24:
Yes, and they got it wrong as it does not require a rotation (0 degrees)

cweitat, 2024-06-24:
They followed the yellow dots as provided in the file as the standard practice as they did with their other customers. And it also impossible to see whether the direction was wrong with just look of it. Moreover, this was only highlighted more than 2 months after it was shipped out

bessman, 2024-06-24:
> They followed the yellow dots as provided in the file as the standard practice

They did not; standard practice is that the yellow dot marks the connection point for pin 1. They have connected pin 3 at the yellow dot.

> it also impossible to see whether the direction was wrong with just look of it.

Incorrect. There are at least two ways to ensure correct orientation with visual inspection:

1. Note the location of the triangular marking next to pin 3, as specified in the datasheet
2. Note that the LED actually turns on when powered (as I believe we instructed them to do?)

cweitat, 2024-06-24:
@bessman Yes. The file given them had the error of  yellow dot placed at pin 3, not pin 1, which is what Padmal brought up earlier messages. So in this case, meaning the Gerber was wrong.

There was no mention of how testing should be done other than LED lighting up. It was raised prior to the production and only the lighting up of LED was mentioned.

For point 2, yes the test was plug in power and see if the LED lights up. No particular instructions was mentioned as to which LED lights up etc. Also, there's no manual for test as well, other than an old one. In this case, the white LED lights up so it's considered as a pass.

CloudyPadmal, 2024-06-24:
I don't know how else to say that it was the manufacturer who messed up the assembly which took us some time to debug 🙆🏻‍♂️

Please don't misinterpret and the production files are still valid and 100% correct.

CloudyPadmal, 2024-06-24:
> And it also impossible to see whether the direction was wrong with just look of it. 

Just looking at it is in fact the visual inspection stage where you identify ICs assembled in wrong orientations. Check my previous comments about silk screen markings. 

This is the standard procedure with PCBWay and JLCPCB.

cweitat, 2024-06-25:
AOI machine file for polarity testing comes from the provided Gerber (which had the dot on pin 3) as well. So the test would have passed any ways.

CloudyPadmal, 2024-06-25:
Dot is in pin 1 as mentioned earlier. 

I'm repeating the same thing and I don't think this discussion yields anything.

cweitat, 2024-06-26:
@CloudyPadmal yes I understand that as well. Therefore I left the communication to the manufacturer with Mario now.

CloudyPadmal, 2024-06-26:
Sounds good. I'm closing this issue as now we know that the manufacturer did not follow the design files correctly and we will manually fix the LEDs with their supposed orientation before shipping out to customers.

closed 2024-06-26 by CloudyPadmal

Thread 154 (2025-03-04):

fossasia/pslab-hardware #154: Missing release of the final v6 as a tagged stable release

froscon2024, 2025-03-04:
The current releases are pre-releases https://github.com/fossasia/pslab-hardware/releases
A stable, final release of the v6 that is in production since over a year would be great for archive and documentation purpose.

bessman, 2025-03-04:
@CloudyPadmal @mariobehling Could you confirm which commit was used for production so we can tag it?

froscon2024, 2025-03-04:
The date code printed on the v6 i have is: 25.12.2023
It was missing the ESP-01 header i could see on some renderings of the v6. I soldered the header in myself to be able to connect and remove the ESP-01 whenever i want.

When i take a look at https://github.com/fossasia/pslab-hardware/commits/pslab-v6/
then i can see that the only two changes that have been merged after 25.12.2023.

The PCB i have is already with the silk screen updates: https://github.com/fossasia/pslab-hardware/pull/150/files
And those got merged January 2024 but the PR is from end of 2023 and looks to be done for production but merged into this repo after producing the PCB's with the PR included.

So i think the production code of the v6 is the code that is recent this days in this repo.
I think when you now make a stable release with the current code, this would be exactly the production version of the v6. You can then remove the older pre-release parts and then there would be just stable v5 and stable v6 release in this repo.

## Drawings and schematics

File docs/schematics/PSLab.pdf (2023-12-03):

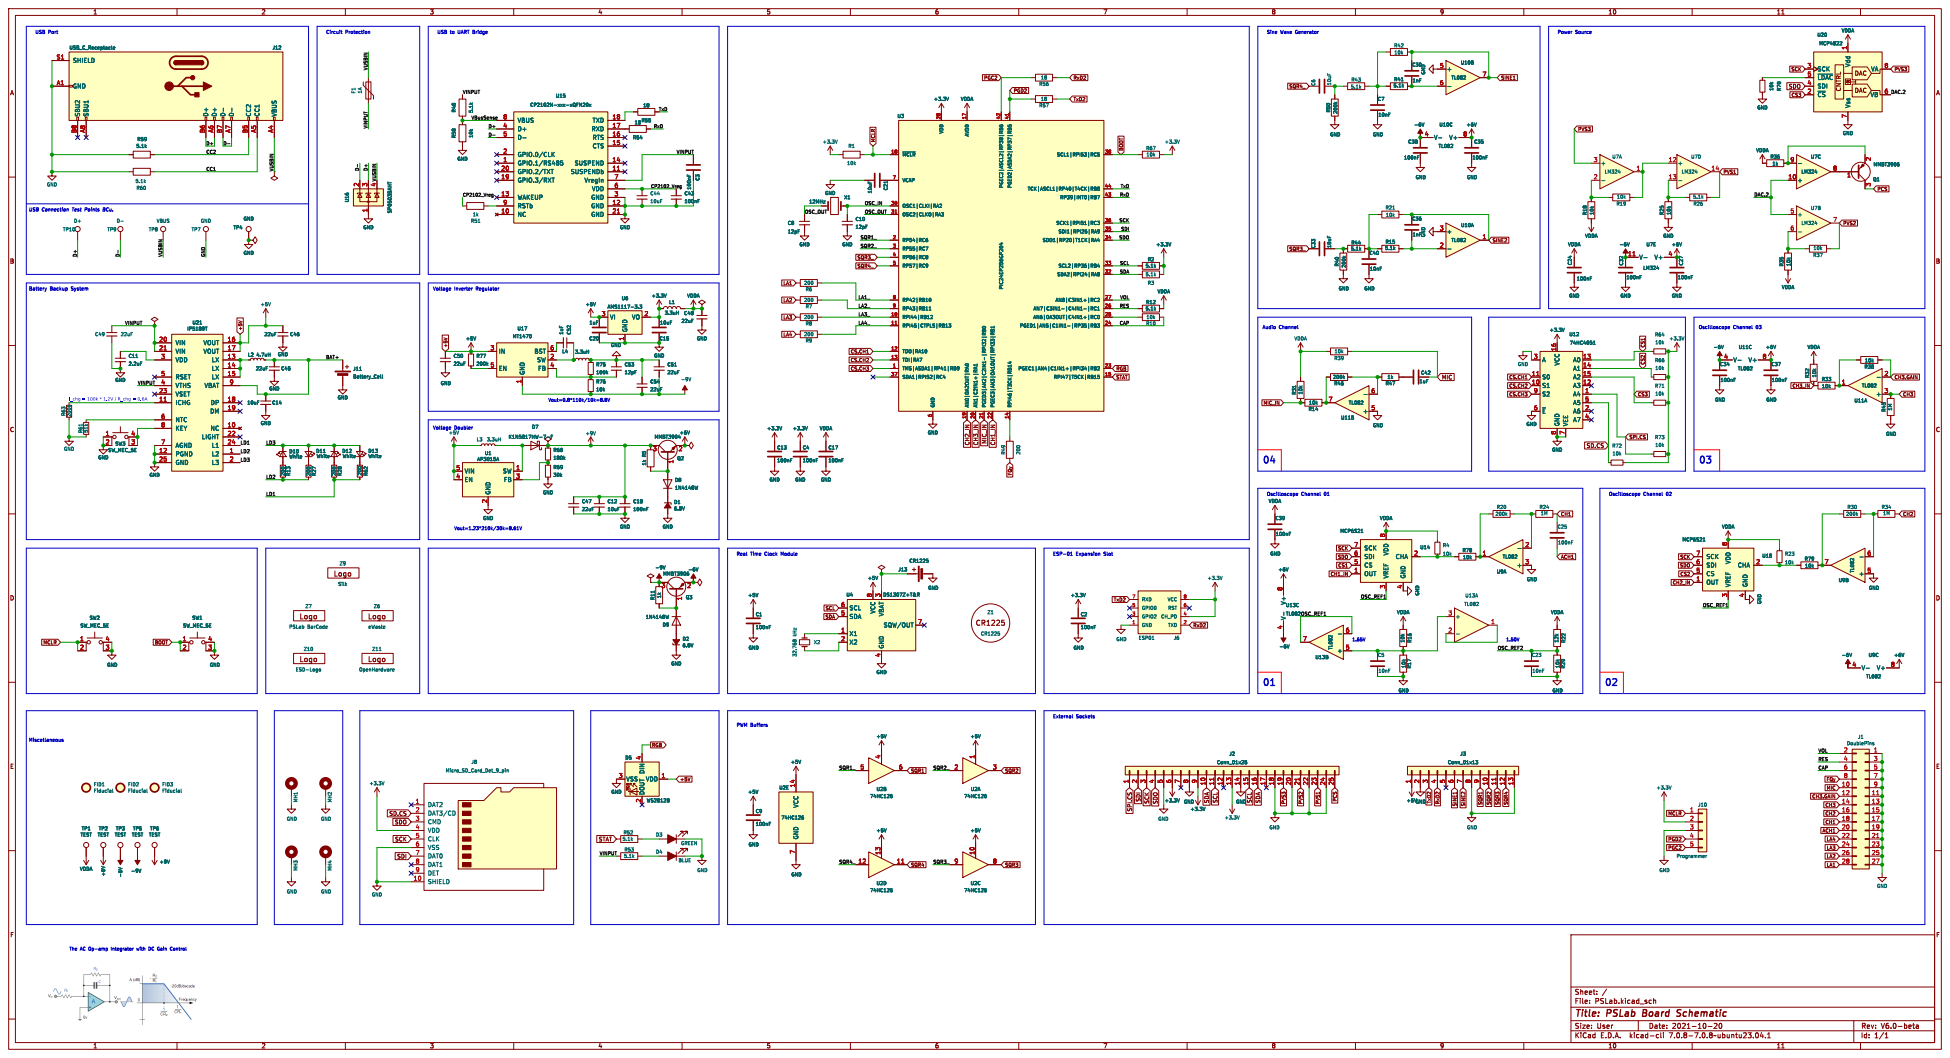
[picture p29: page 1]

Circuit Protection Battery Backup System

USB to UART Bridge

4 SDA 5 SCL 6 SQW/OUT 7 VCC

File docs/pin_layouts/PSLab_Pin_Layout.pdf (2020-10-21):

# Pocket Science Lab V6

# Pin Layout Diagram

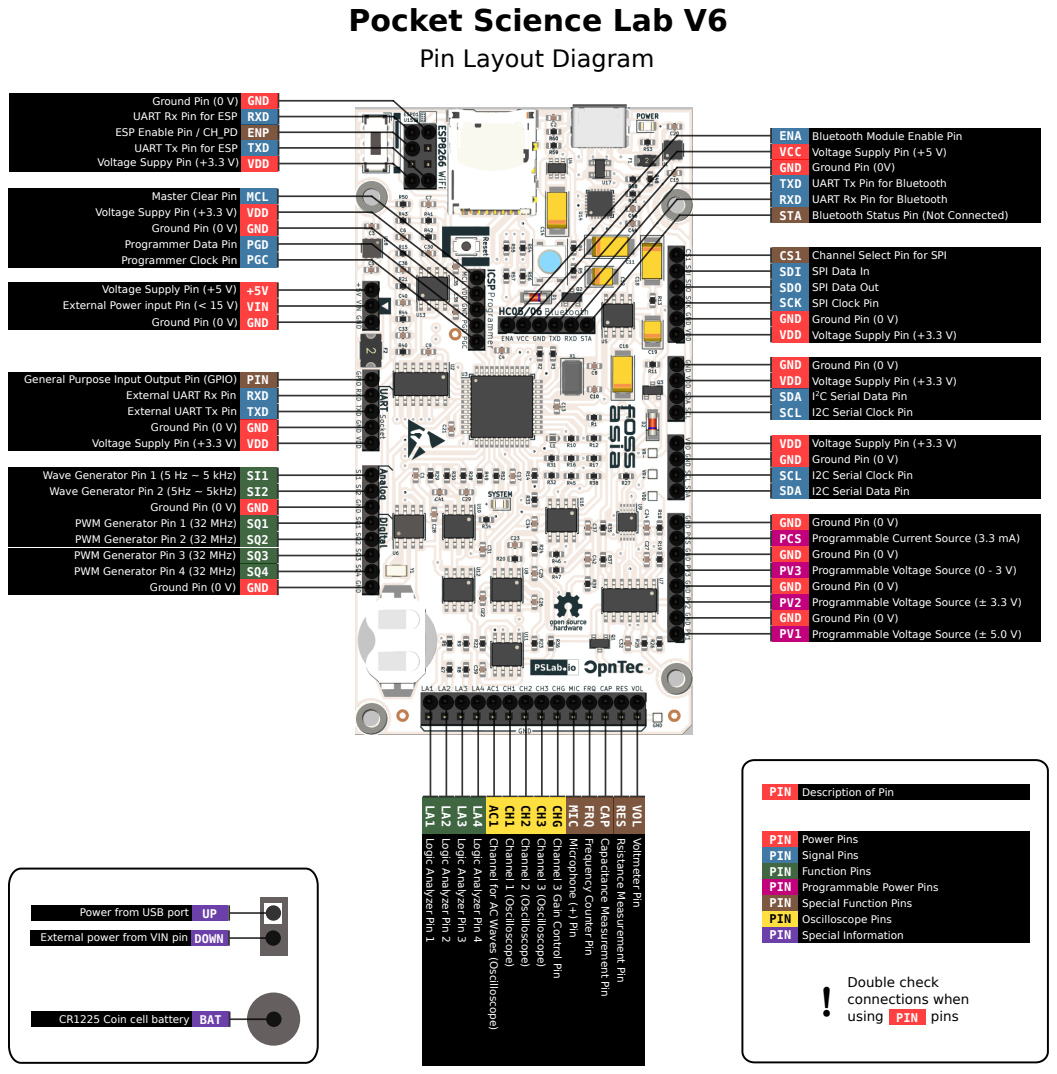
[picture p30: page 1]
2 SDA; C Serial Data Pin; Channel 1 (Oscilloscope) CH1; Channel 2 (Oscilloscope) CH2; Channel 3 (Oscilloscope) CH3; PIN; using; pins

Ground Pin (0 V) GND
UART Rx Pin for ESP RXD
ESP Enable Pin / CH_PD ENP
UART Tx Pin for ESP TXD
Voltage Suppy Pin (+3.3 V) VDD

ENA Bluetooth Module Enable Pin
VCC Voltage Supply Pin (+5 V)
GND Ground Pin (0V)
TXD UART Tx Pin for Bluetooth
RXD UART Rx Pin for Bluetooth
STA Bluetooth Status Pin (Not Connected)

Master Clear Pin MCL

Programmer Data Pin PGD
Programmer Clock Pin PGC

CS1 Channel Select Pin for SPI
SDI SPI Data In
SDO SPI Data Out
SCK SPI Clock Pin
GND Ground Pin (0 V)
VDD Voltage Supply Pin (+3.3 V)

Voltage Supply Pin (+5 V) +5V

External Power input Pin (< 15 V) VIN

SCL I2C Serial Clock Pin

General Purpose Input Output Pin (GPIO) PIN

External UART Rx Pin RXD
External UART Tx Pin TXD

Voltage Supply Pin (+3.3 V) VDD

SDA I2C Serial Data Pin

Wave Generator Pin 1 (5 Hz ~ 5 kHz) SI1
Wave Generator Pin 2 (5Hz ~ 5kHz) SI2

PWM Generator Pin 1 (32 MHz) SQ1
PWM Generator Pin 2 (32 MHz) SQ2
PWM Generator Pin 3 (32 MHz) SQ3
PWM Generator Pin 4 (32 MHz) SQ4

PCS Programmable Current Source (3.3 mA)
PV3 Programmable Voltage Source (0 - 3 V)
PV2 Programmable Voltage Source (± 3.3 V)
PV1 Programmable Voltage Source (± 5.0 V)

PIN Description of Pin

Logic Analyzer Pin 1 LA1

Logic Analyzer Pin 2 LA2

Logic Analyzer Pin 3 LA3

Logic Analyzer Pin 4 LA4

Channel for AC Waves (Oscilloscope) AC1

Channel 3 Gain Control Pin CHG

Microphone (+) Pin MIC

Frequency Counter Pin FRQ

Capacitance Measurement Pin CAP

Rsistance Measurement Pin RES

Voltmeter Pin VOL

PIN Power Pins
PIN Signal Pins
PIN Function Pins
PIN Programmable Power Pins
PIN Special Function Pins
PIN Oscilloscope Pins
PIN Special Information
Double check
connections when

Power from USB port UP

External power from VIN pin DOWN

CR1225 Coin cell battery BAT

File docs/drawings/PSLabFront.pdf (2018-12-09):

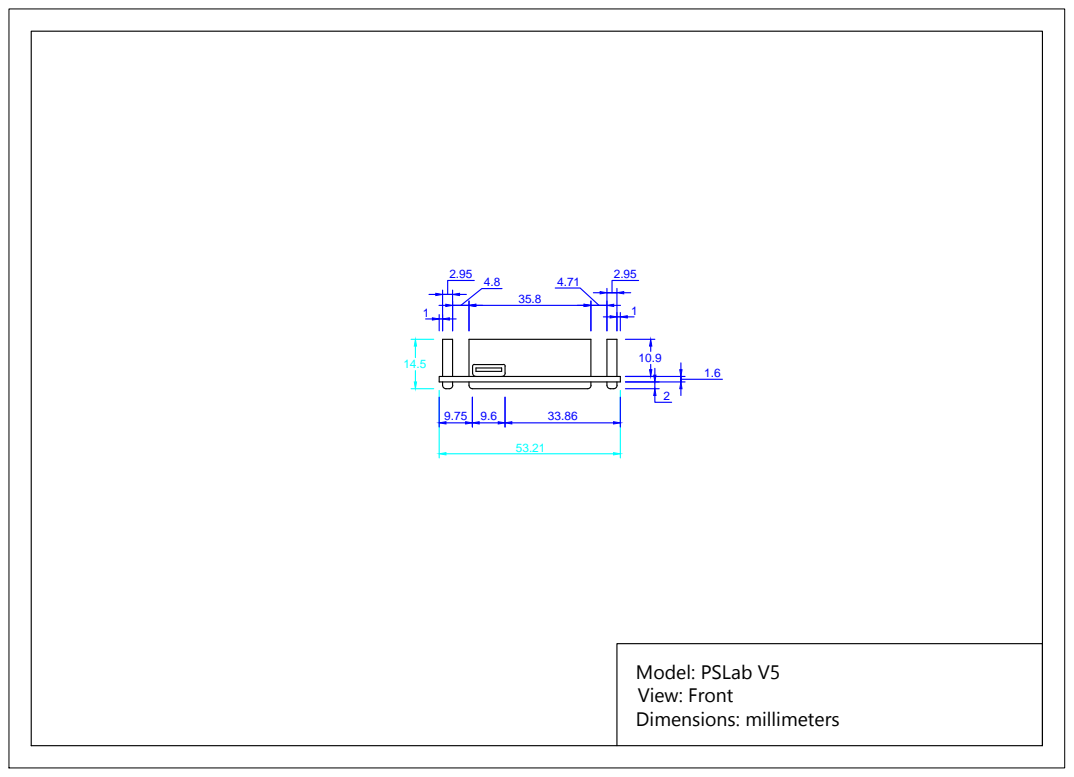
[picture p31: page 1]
Model: PSLab V5 View: Front Dimensions: millimeters

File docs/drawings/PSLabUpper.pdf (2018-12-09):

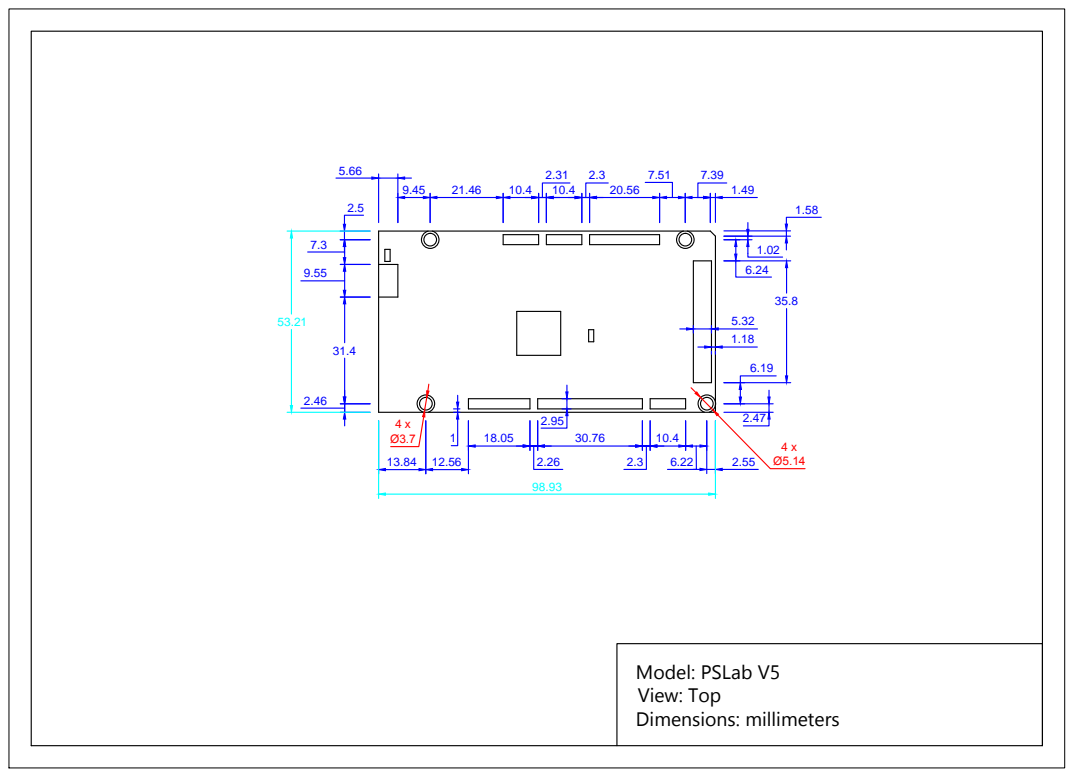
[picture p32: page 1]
Model: PSLab V5 View: Top Dimensions: millimeters

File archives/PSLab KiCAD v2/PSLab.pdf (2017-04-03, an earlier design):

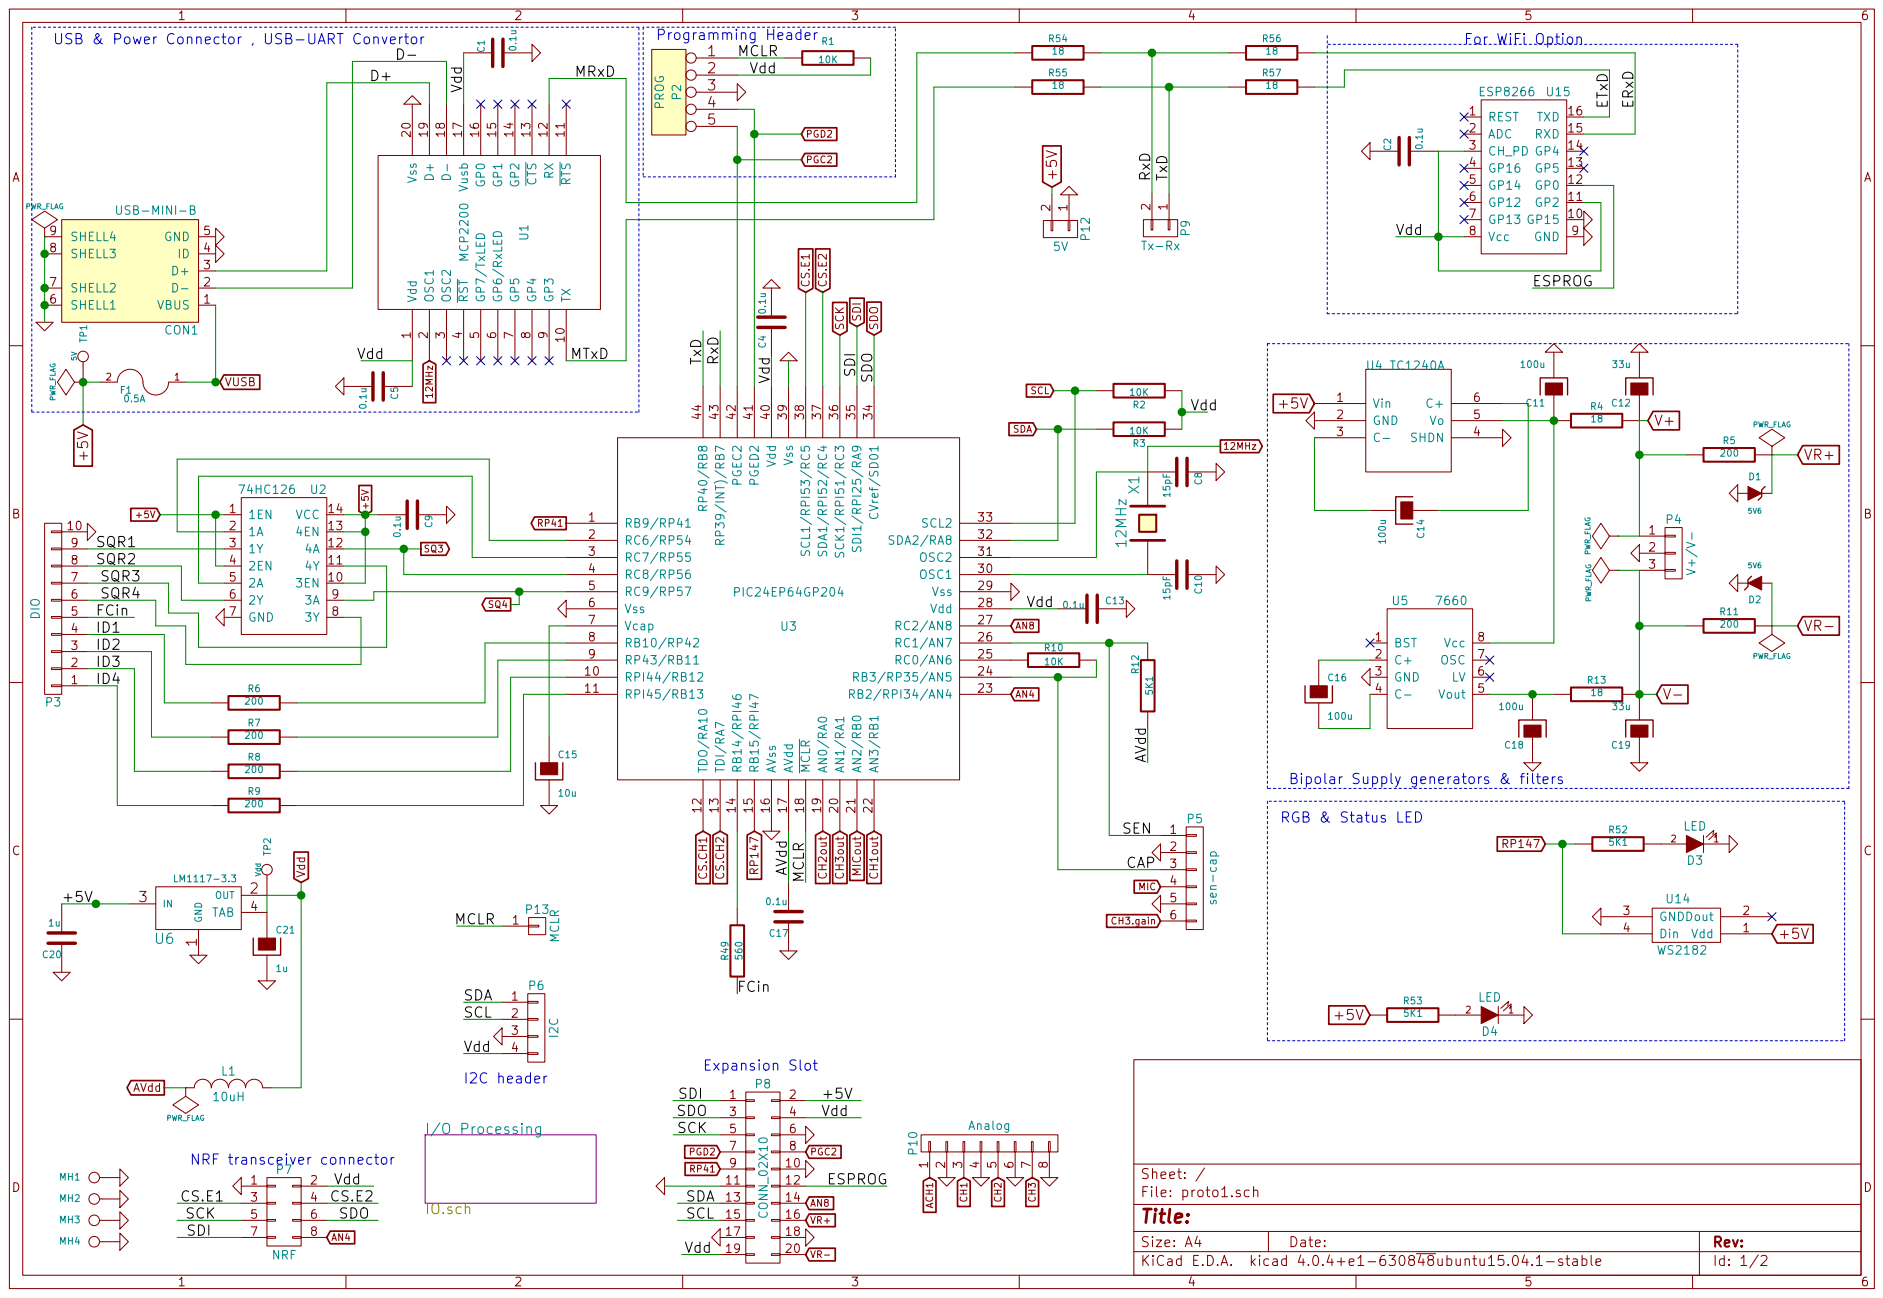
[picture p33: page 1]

9 TX 10 Vss 20 RTS 11 RX 12 CTS 13 GP2 14 GP1 15 GP0 16 Vusb 17 D- 18 D+ 19 U1 MCP2200 1

1 OSC1
File: proto1.sch Sheet: / Vdd

Bipolar Supply generators & filters
6 P5 sen-cap

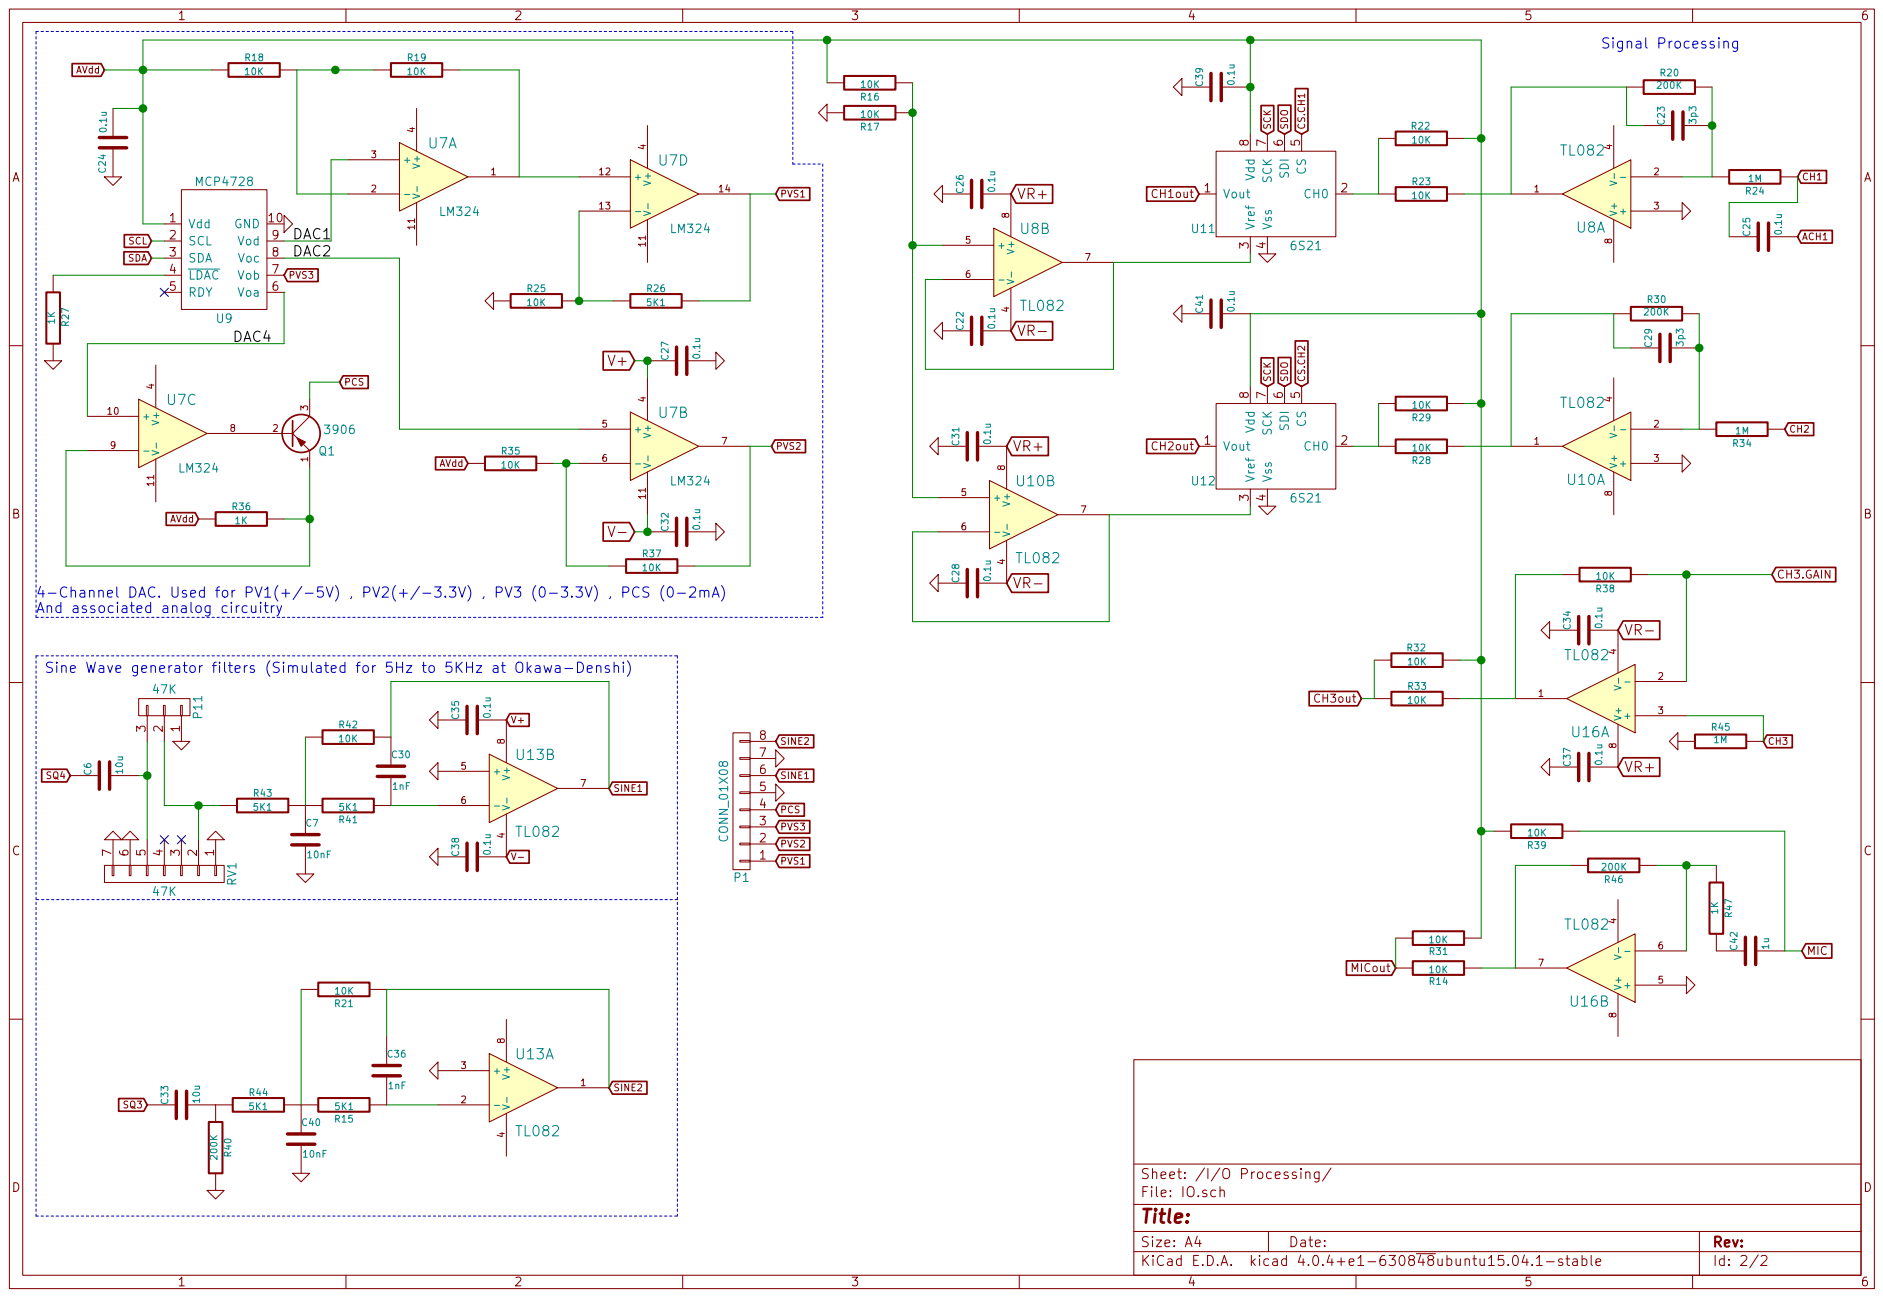
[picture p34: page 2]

47K 4-Channel DAC. Used for PV1(+/-5V) , PV2(+/-3.3V) , PV3 (0-3.3V) , PCS (0-2mA)
And associated analog circuitry

Sine Wave generator filters (Simulated for 5Hz to 5KHz at Okawa-Denshi)

Id: 2/2 Title: File: IO.sch Sheet: /I/O Processing/

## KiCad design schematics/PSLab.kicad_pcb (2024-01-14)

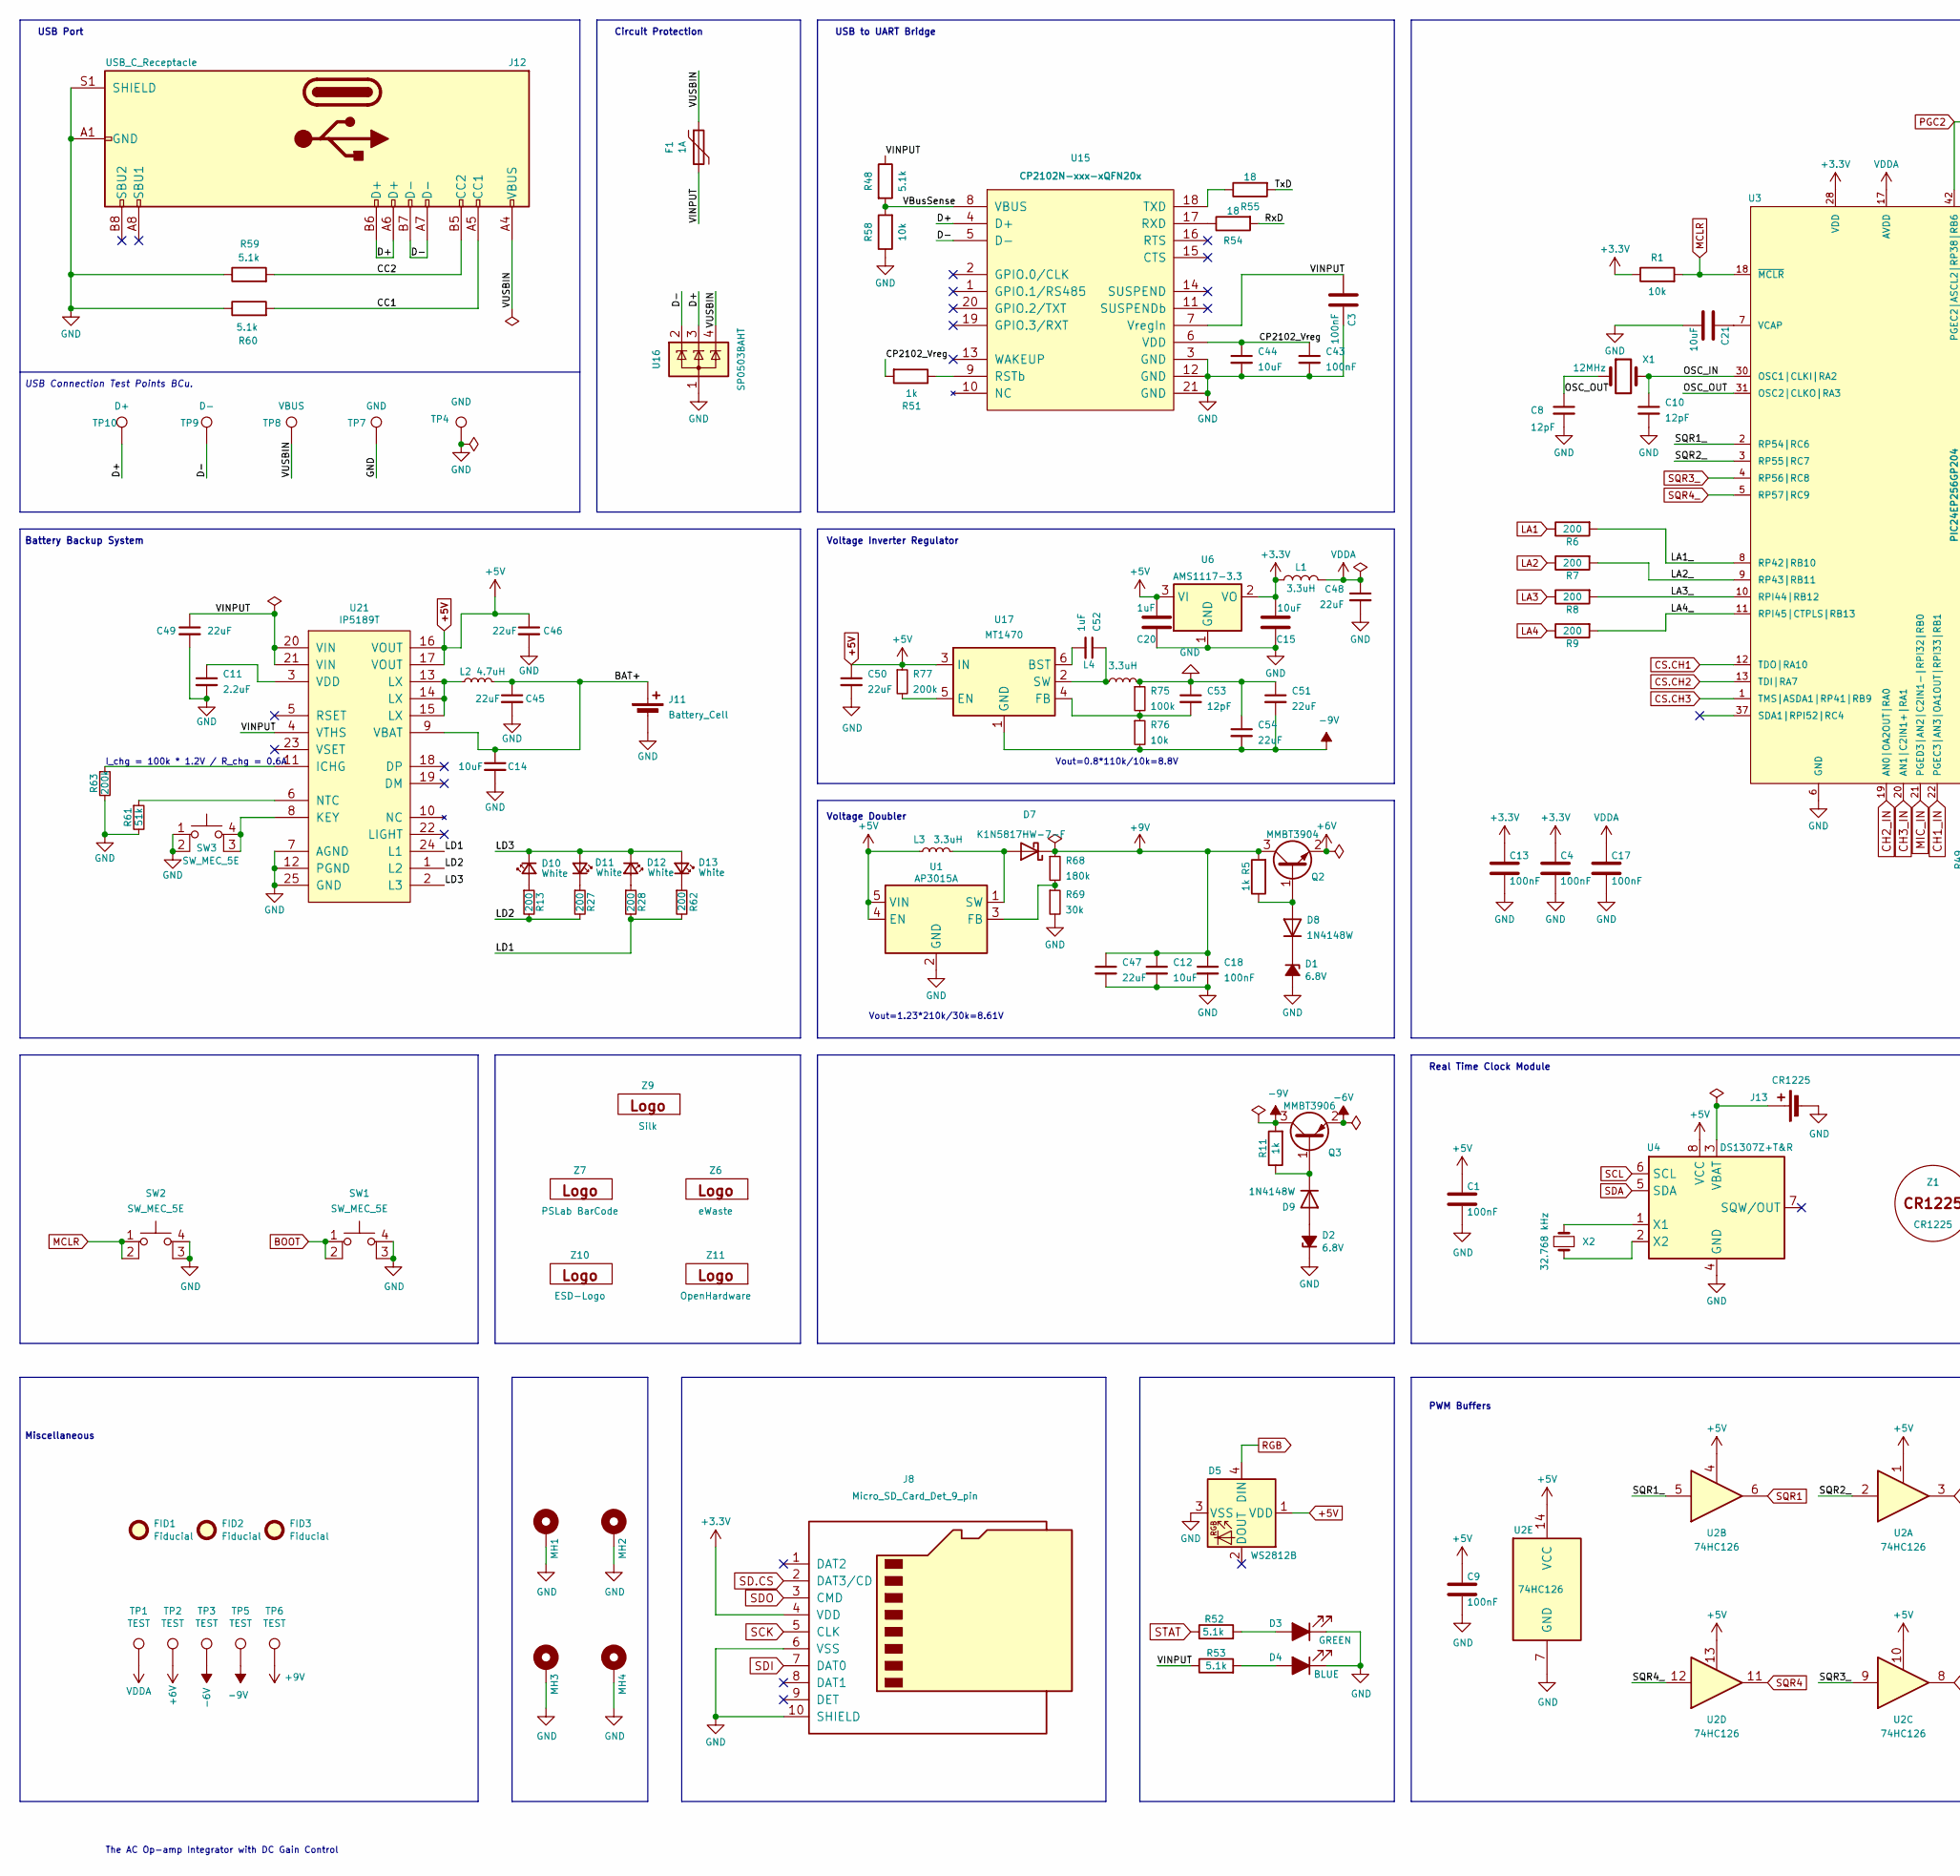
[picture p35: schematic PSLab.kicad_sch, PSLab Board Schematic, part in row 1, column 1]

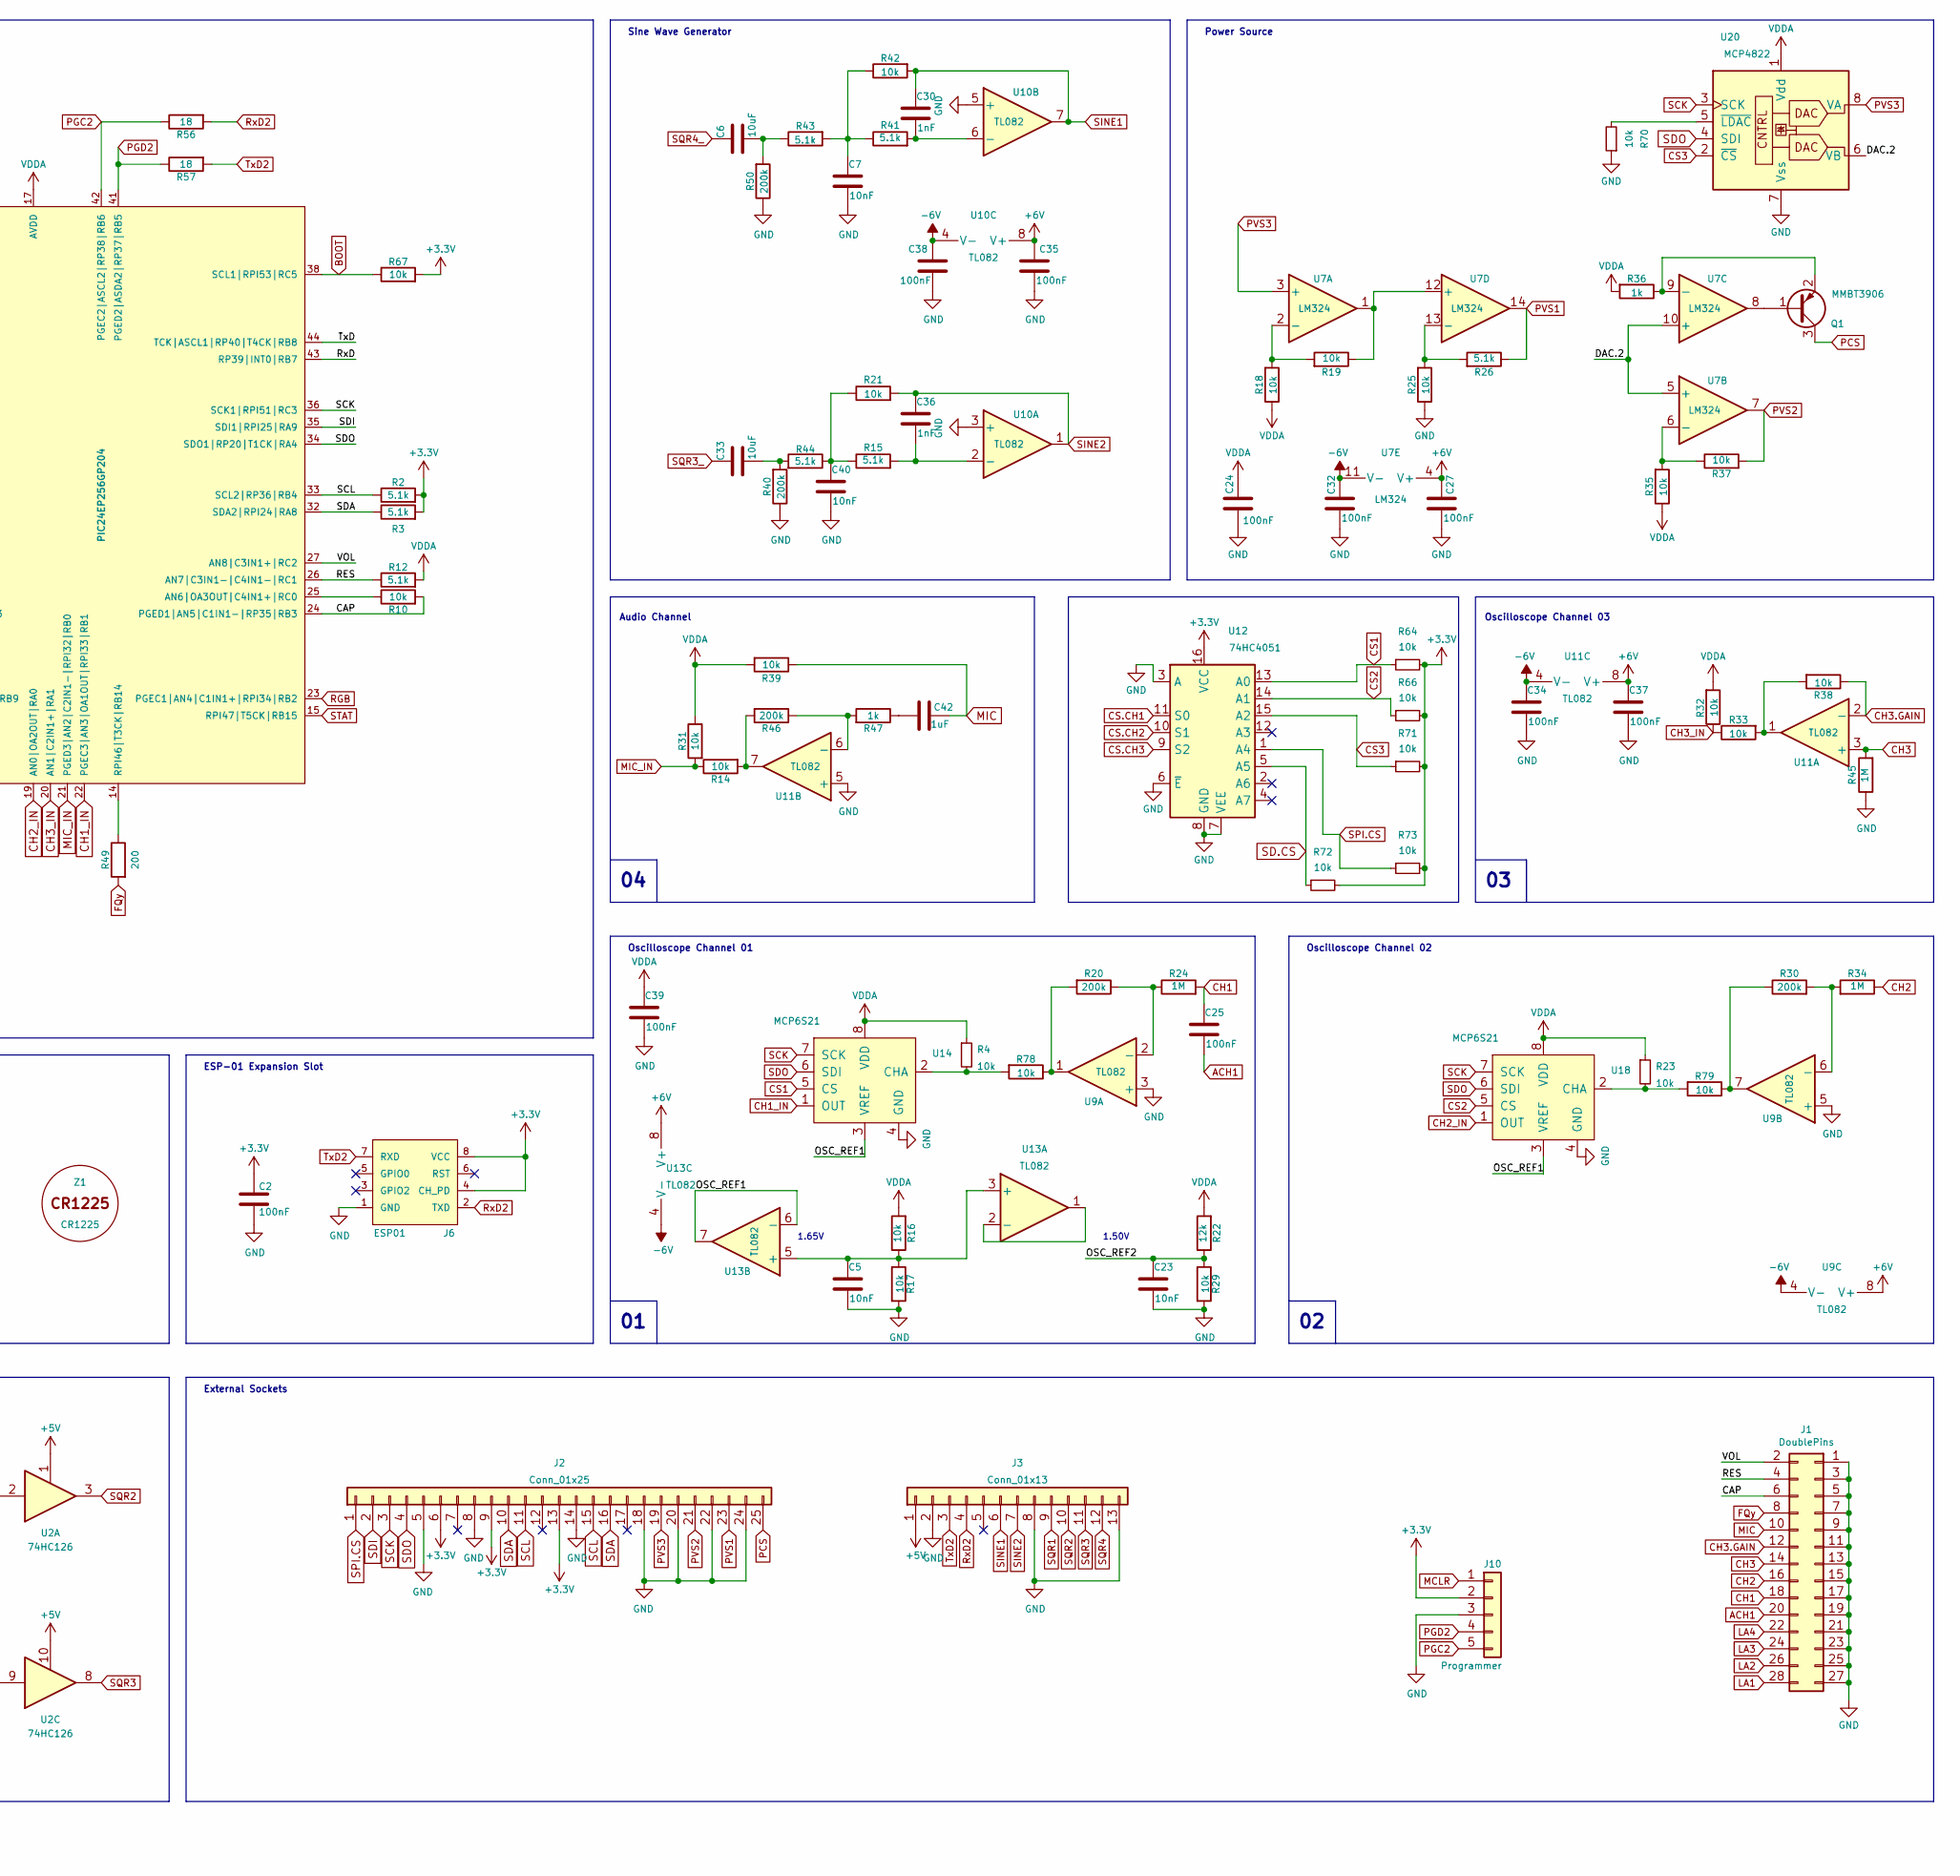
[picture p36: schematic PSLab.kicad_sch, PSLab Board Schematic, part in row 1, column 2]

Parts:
C1, C2, C3, C4, C9, C13, C17, C24, C25, C27, C32, C34, C35, C37, C38, C39: 100nF; C_0603_1608Metric; PartNumber C0603C104J4RACTU
C5, C23: 10nF; C_0603_1608Metric; PartNumber C0603C104J4RACTU
C6, C15, C21, C33: 10uF; C_0603_1608Metric; PartNumber EMK107BC6106MA-T
C7, C40: 10nF; C_0603_1608Metric; PartNumber VJ0603Y103JXJPW1BC
C8, C10, C53: 12pF; C_0603_1608Metric
C11: 2.2uF; C_0603_1608Metric
C12, C14, C44: 10uF; C_0603_1608Metric
C18, C43: 100nF; C_0603_1608Metric
C20, C42: 1uF; C_0603_1608Metric; PartNumber 0603YD105KAT2A
C30, C36: 1nF; C_0603_1608Metric; PartNumber C0603C102J5RACAUTO
C45, C46, C47, C48, C49, C50, C51, C54: 22uF; C_0603_1608Metric
C52: 1uF; C_0603_1608Metric
D1, D2: 6.8V; D_MiniMELF; PartNumber BZV55B6V8 L1
D3: GREEN; LED_0805_2012Metric; PartNumber HSMQ-C170-T0000
D4: BLUE; LED_0805_2012Metric; PartNumber HSMR-C170-R0000
D5: WS2812B; LED_WS2812B_PLCC4_5.0x5.0mm_P3.2mm; PartNumber WS2812B
D7: K1N5817HW-7-F; D_SOD-123
D8: 1N4148W; D_MiniMELF
D9: 1N4148W; D_SOD-123
D10, D11, D12, D13: White; LED_0603_1608Metric
F1: 1A; Fuse_1206_3216Metric; PartNumber 0ZCJ0025FF2E
FID1, FID2, FID3: Fiducial; Fiducial_0.5mm_Mask1.5mm; PartNumber N/A
J1: DoublePins; PinSocket_2x14_P2.54mm_Vertical; PartNumber SSW-114-01-T-D
J2: Conn_01x25; PinSocket_1x25_P2.54mm_Vertical
J3: Conn_01x13; PinSocket_1x13_P2.54mm_Vertical
J6: ESP01; ESP-01; PartNumber SSW-104-01-T-D
J8: Micro_SD_Card_Det_9_pin; TF-015
J10: Programmer; PinSocket_1x05_P2.54mm_Vertical
J11: Battery_Cell; 2.0mm_connector_edge
J12: USB_C_Receptacle; USB_C_Receptacle_12pin_SMT; PartNumber U262-161N-4BVC11
J13: CR1225; BatteryHolder_A359; PartNumber BAT-HLD-012-SMT
L1: 3.3uH; L_Taiyo-Yuden_MD-2020; PartNumber SMNR201610-3R3MT
L2: 4.7uH; L_Taiyo-Yuden_MD-2020; Part Number SMNR201610-4R7MT
L3: 3.3uH; L_Taiyo-Yuden_MD-2020
L4: 3.3uH; L_Taiyo-Yuden_MD-2020; Part Number SMNR201610-3R3MT
MH1, MH2, MH3: M; OneSided_MPad; PartNumber 9774030360R
MH4: M; TwoSided_MPad; PartNumber 9774030360R
Q1, Q3: MMBT3906; SOT-23; PartNumber MMBT3906-7-F
Q2: MMBT3904; SOT-23; PartNumber MMBT3904,215
R1, R10, R14, R16, R17, R18, R19, R21, R25, R29, R31, R32, R33, R35, R37, R38, R39, R42, R58, R67, R78, R79: 10k; R_0603_1608Metric; PartNumber RR0816P-103-D
R2, R3, R12, R15, R26, R41, R43, R44, R48, R52, R53, R59, R60: 5.1k; R_0603_1608Metric; PartNumber RR0816P-512-D
R4, R23, R64, R66, R70, R71, R72, R73, R76: 10k; R_0603_1608Metric
R5, R11, R36, R47, R51: 1k; R_0603_1608Metric; PartNumber RR0816P-102-D
R6, R7, R8, R9, R49: 200; R_0603_1608Metric; PartNumber RR0816P-201-D
R13, R27, R28, R62: 200; R_0603_1608Metric
R20, R30, R40, R46, R50: 200k; R_0603_1608Metric; PartNumber RR0816P-204-D
R22: 12k; R_0603_1608Metric; PartNumber RR0816P-103-D
R24, R34, R45: 1M; R_0603_1608Metric; PartNumber RT0603FRE071ML
R54, R55, R56, R57: 18; R_0603_1608Metric; PartNumber RR0816Q-180-D
R61: 51k; R_0603_1608Metric
R63, R77: 200k; R_0603_1608Metric
R68: 180k; R_0603_1608Metric
R69: 30k; R_0603_1608Metric
R75: 100k; R_0603_1608Metric
SW1, SW2, SW3: SW_MEC_5E; button_SPST_3x4x2.5
TP1, TP2, TP3, TP5, TP6: TEST; Test_Point_0.8mm
TP4, TP7: GND; TestPoint_Pad_1.0x1.0mm
TP8: VBUS; TestPoint_Pad_1.0x1.0mm
TP9: D-; TestPoint_Pad_1.0x1.0mm
TP10: D+; TestPoint_Pad_1.0x1.0mm
U1: AP3015A; SOT-23-5
U2: 74HC126; TSSOP-14_4.4x5mm_P0.65mm; PartNumber SN74HC126PW
U3: PIC24EP256GP204; TQFP-44_10x10mm_P0.8mm; PartNumber PIC24EP256GP204-I/PT
U4: DS1307Z+T&R; SOIC-8_3.9x4.9mm_P1.27mm; PartNumber DS1307Z+T&R
U6: AMS1117-3.3; SOT-223-3_TabPin2
U7: LM324; TSSOP-14_4.4x5mm_P0.65mm; PartNumber LM324APT
U9, U10, U11: TL082; SOIC-8_3.9x4.9mm_P1.27mm; PartNumber TL082CDR
U12: 74HC4051; TSSOP-16_4.4x5mm_P0.65mm
U13: TL082; SOIC-8_3.9x4.9mm_P1.27mm
U14, U18: MCP6S21; SOIC-8_3.9x4.9mm_P1.27mm; PartNumber MCP6S21-I/SN
U15: CP2102N-xxx-xQFN20x; QFN-20_EP_3x3_Pitch0.5mm
U16: SP0503BAHT; SOT-143; PartNumber SP0503BAHTG
U17: MT1470; SOT-23-6
U20: MCP4822; SOIC-8_3.9x4.9mm_P1.27mm
U21: IP5189T; QFN-24-1EP_4x4mm_P0.5mm_EP2.6x2.6mm
X1: 12MHz; Crystal_SMD_5032-2Pin_5.0x3.2mm
X2: 32.768 kHz; Crystal_SMD_3215-2Pin_3.2x1.5mm; PartNumber ABS07-166-32.768KHZ-T
Z1: CR1225; Battery_CR1225; PartNumber IEC-CR1225
Z6: eWaste; WEEE-Logo_4.2x6mm_SilkScreen
Z7: PSLab BarCode; Barcode
Z9: Silk; PSLab_SilkScreen
Z10: ESD-Logo; ESD-Logo_6.6x6mm_SilkScreen
Z11: OpenHardware; OSHW-Logo_5.7x6mm_SilkScreen

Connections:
+3.3V: C2.1, C4.1, C13.1, C15.2, J2.6, J2.9, J2.13, J6.4 (CH_PD), J6.8 (VCC), J8.4 (VDD), J10.2, L1.2, R1.1, R2.2, R3.2, R64.2, R66.2, R67.2, R71.2, R72.2, R73.2, U3.28 (VDD), U3.40 (VDD), U6.2 (VO), U12.16 (VCC)
+5V: C1.1, C9.1, C20.2, C46.1, C50.1, D5.1 (VDD), J3.1, L3.1, R77.1, U1.4 (EN), U1.5 (VIN), U2.1, U2.4, U2.10, U2.13, U2.14 (VCC), U4.8 (VCC), U6.3 (VI), U17.3 (IN), U21.16 (VOUT), U21.17 (VOUT)
+6V: C27.1, C35.1, C37.1, Q2.2 (E), TP2.1, U7.4 (V+), U9.8 (V+), U10.8 (V+), U11.8 (V+), U13.8 (V+)
+9V: C12.1, C18.1, C47.1, D7.1 (K), Q2.3 (C), R5.2, R68.1, TP6.1
-6V: C32.1, C34.1, C38.1, Q3.2 (E), TP3.1, U7.11 (V-), U9.4 (V-), U10.4 (V-), U11.4 (V-), U13.4 (V-)
-9V: C51.2, C54.2, Q3.3 (C), R11.2, R76.2, TP5.1, U17.1 (GND)
/BAT+: C14.1, C45.1, J11.1 (+), L2.2, U21.9 (VBAT)
/CAP: J1.6, R10.2, U3.24 (PGED1|AN5|C1IN1-|RP35|RB3)
/CC1: J12.A5 (CC1), R60.2
/CC2: J12.B5 (CC2), R59.2
/CP2102_Vreg: C43.1, C44.1, R51.2, U15.6 (VDD)
/D+: J12.A6 (D+), J12.B6 (D+), TP10.1, U15.4 (D+), U16.3 (K)
/D-: J12.A7 (D-), J12.B7 (D-), TP9.1, U15.5 (D-), U16.2 (K)
/DAC.2: U7.5 (+), U7.10 (+), U20.6 (VB)
/LA1_: R6.2, U3.8 (RP42|RB10)
/LA2_: R7.2, U3.9 (RP43|RB11)
/LA3_: R8.2, U3.10 (RPI44|RB12)
/LA4_: R9.2, U3.11 (RPI45|CTPLS|RB13)
/LD1: R28.2, R62.2, U21.24 (L1)
/LD2: R13.2, R27.2, U21.1 (L2)
/LD3: D10.1 (K), D11.2 (A), D12.1 (K), D13.2 (A), U21.2 (L3)
/OSC_IN: C10.1, U3.30 (OSC1|CLKI|RA2), X1.2
/OSC_OUT: C8.1, U3.31 (OSC2|CLKO|RA3), X1.1
/OSC_REF1: U13.6 (-), U13.7, U14.3 (VREF), U18.3 (VREF)
/OSC_REF2: C23.1, R22.1, R29.1
/RES: J1.4, R12.1, U3.26 (AN7|C3IN1-|C4IN1-|RC1)
/RxD: R54.2, U3.43 (RP39|INT0|RB7)
/SQR1_: U2.5, U3.2 (RP54|RC6)
/SQR2_: U2.2, U3.3 (RP55|RC7)
/TxD: R55.2, U3.44 (TCK|ASCL1|RP40|T4CK|RB8)
/VBusSense: R48.2, R58.2, U15.8 (VBUS)
/VINPUT: C3.2, C49.1, F1.2, R48.1, R53.1, U15.7 (VregIn), U21.4 (VTHS), U21.20 (VIN), U21.21 (VIN)
/VOL: J1.2, U3.27 (AN8|C3IN1+|RC2)
/VUSBIN: F1.1, J12.A4 (VBUS), J12.A9 (VBUS), J12.B4 (VBUS), J12.B9 (VBUS), TP8.1, U16.4 (K)
ACH1: C25.2, J1.20
BOOT: R67.1, SW1.1, SW1.2, U3.38 (SCL1|RPI53|RC5)
CH1: C25.1, J1.18, R24.2
CH1_IN: U3.22 (PGEC3|AN3|OA1OUT|RPI33|RB1), U14.1 (OUT)
CH2: J1.16, R34.1
CH2_IN: U3.19 (AN0|OA2OUT|RA0), U18.1 (OUT)
CH3: J1.14, R45.2, U11.3 (+)
CH3.GAIN: J1.12, R38.1, U11.2 (-)
CH3_IN: R32.1, R33.1, U3.20 (AN1|C2IN1+|RA1)
CS1: R64.1, U12.13 (A0), U14.5 (CS)
CS2: R66.1, U12.14 (A1), U18.5 (CS)
CS3: R71.1, U12.15 (A2), U20.2 (~CS)
CS.CH1: U3.12 (TDO|RA10), U12.11 (S0)
CS.CH2: U3.13 (TDI|RA7), U12.10 (S1)
CS.CH3: U3.1 (TMS|ASDA1|RP41|RB9), U12.9 (S2)
FQy: J1.8, R49.2
GND: C1.2, C2.2, C3.1, C4.2, C5.2, C7.2, C8.2, C9.2, C10.2, C11.2, C12.2, C13.2, C14.2, C15.1, C17.2, C18.2, C20.1, C21.2, C23.2, C24.1, C27.2, C32.2, C34.2, C35.2, C37.2, C38.2, C39.2, C40.2, C43.2, C44.2, C45.2, C46.2, C47.2, C48.2, C49.2, C50.2, C51.1, C53.1, C54.1, D1.2 (A), D2.1 (K), D3.1 (K), D4.1 (K), D5.3 (VSS), J1.1, J1.3, J1.5, J1.7, J1.9, J1.11, J1.13, J1.15, J1.17, J1.19, J1.21, J1.23, J1.25, J1.27, J2.5, J2.8, J2.14, J2.18, J2.20, J2.22, J2.24, J3.2, J3.8, J3.13, J6.1 (GND), J8.6 (VSS), J8.10 (SHIELD), J10.3, J11.2 (-), J12.A1 (GND), J12.A12 (GND), J12.B1 (GND), J12.B12 (GND), J12.S1 (SHIELD), J13.2 (-), L4.2, MH1.1, MH2.1, MH3.1, MH4.1, R17.2, R25.1, R29.2, R40.1, R45.1, R50.1, R58.1, R59.1, R60.1, R61.2, R63.2, R69.2, R70.1, R75.1, SW1.3 (K), SW1.4 (A), SW2.3 (K), SW2.4 (A), SW3.1, SW3.2, TP4.1, TP7.1, U1.2 (GND), U2.7 (GND), U3.6 (GND), U3.16 (GND), U3.29 (GND), U3.39 (GND), U4.4 (GND), U6.1 (GND), U9.3 (+), U9.5 (+), U10.3 (+), U10.5 (+), U11.5 (+), U12.3 (A), U12.6 (~E), U12.7 (VEE), U12.8 (GND), U14.4 (GND), U15.3 (GND), U15.12 (GND), U15.21 (GND), U16.1 (A), U18.4 (GND), U20.7 (Vss), U21.7 (AGND), U21.12 (PGND), U21.25 (GND)
LA1: J1.28, R6.1
LA2: J1.26, R7.1
LA3: J1.24, R8.1
LA4: J1.22, R9.1
MCLR: J10.1, R1.2, SW2.1, SW2.2, U3.18 (~MCLR)
MIC: C42.2, J1.10, R39.1
MIC_IN: R14.1, R31.2, U3.21 (PGED3|AN2|C2IN1-|RPI32|RB0)
unnamed: C6.2, R43.1, R50.2
unnamed: C7.1, R41.1, R42.1, R43.2
unnamed: C33.2, R40.2, R44.2
unnamed: C40.1, R15.1, R21.1, R44.1
unnamed: C42.1, R47.1
unnamed: D1.1 (K), D8.1 (K)
unnamed: D2.2 (A), D9.2 (A)
unnamed: D3.2 (A), R52.2
unnamed: D4.2 (A), R53.2
unnamed: D7.2 (A), L3.2, U1.1 (SW)
unnamed: D8.2 (A), Q2.1 (B), R5.1
unnamed: D9.1 (K), Q3.1 (B), R11.1
unnamed: D10.2 (A), R13.1
unnamed: D11.1 (K), R27.1
unnamed: D12.2 (A), R28.1
unnamed: D13.1 (K), R62.1
unnamed: J13.1 (+), U4.3 (VBAT)
unnamed: L2.1, U21.13 (LX), U21.14 (LX), U21.15 (LX)
unnamed: Q1.1 (B), U7.8
unnamed: Q1.2 (E), R36.1, U7.9 (-)
unnamed: R14.2, R46.2, U11.7
unnamed: R20.2, R78.1, U9.1
unnamed: R30.1, R79.1, U9.7
unnamed: R33.2, R38.2, U11.1
unnamed: SW3.3 (K), SW3.4 (A), U21.8 (KEY)
unnamed: R68.2, R69.1, U1.3 (FB)
unnamed: R10.1, U3.25 (AN6|OA3OUT|C4IN1+|RC0)
unnamed: R49.1, U3.14 (RPI46|T3CK|RB14)
unnamed: C21.1, U3.7 (VCAP)
unnamed: U4.1 (X1), X2.1
unnamed: U4.2 (X2), X2.2
unnamed: R18.2, R19.2, U7.2 (-)
unnamed: R35.2, R37.1, U7.6 (-)
unnamed: R19.1, U7.1, U7.12 (+)
unnamed: R25.2, R26.2, U7.13 (-)
unnamed: R20.1, R24.1, U9.2 (-)
unnamed: R30.2, R34.2, U9.6 (-)
unnamed: C36.2, R15.2, U10.2 (-)
unnamed: C30.2, R41.2, U10.6 (-)
unnamed: R46.1, R47.2, U11.6 (-)
unnamed: C5.1, R16.1, R17.1, U13.3 (+), U13.5 (+)
unnamed: U13.1, U13.2 (-)
unnamed: R4.2, R78.2, U14.2 (CHA)
unnamed: R51.1, U15.9 (RSTb)
unnamed: R54.1, U15.17 (RXD)
unnamed: R55.1, U15.18 (TXD)
unnamed: C52.2, U17.6 (BST)
unnamed: R77.2, U17.5 (EN)
unnamed: C53.2, R75.2, R76.1, U17.4 (FB)
unnamed: C52.1, L4.1, U17.2 (SW)
unnamed: R23.2, R79.2, U18.2 (CHA)
unnamed: R70.2, U20.5 (~LDAC)
unnamed: R63.1, U21.11 (ICHG)
unnamed: R61.1, U21.6 (NTC)
unnamed: C11.1, U21.3 (VDD)
PCS: J2.25, Q1.3 (C)
PGC2: J10.5, R56.1, U3.42 (PGEC2|ASCL2|RP38|RB6)
PGD2: J10.4, R57.1, U3.41 (PGED2|ASDA2|RP37|RB5)
PVS1: J2.23, R26.1, U7.14
PVS2: J2.21, R37.2, U7.7
PVS3: J2.19, U7.3 (+), U20.8 (VA)
RGB: D5.4 (DIN), U3.23 (PGEC1|AN4|C1IN1+|RPI34|RB2)
RxD2: J3.4, J6.2 (TXD), R56.2
SCK: J2.3, J8.5 (CLK), U3.36 (SCK1|RPI51|RC3), U14.7 (SCK), U18.7 (SCK), U20.3 (SCK)
SCL: J2.11, J2.15, R2.1, U3.33 (SCL2|RP36|RB4), U4.6 (SCL)
SD.CS: J8.2 (DAT3/CD), R72.1, U12.5 (A5)
SDA: J2.10, J2.16, R3.1, U3.32 (SDA2|RPI24|RA8), U4.5 (SDA)
SDI: J2.2, J8.7 (DAT0), U3.35 (SDI1|RPI25|RA9)
SDO: J2.4, J8.3 (CMD), U3.34 (SDO1|RP20|T1CK|RA4), U14.6 (SDI), U18.6 (SDI), U20.4 (SDI)
SINE1: C30.1, J3.6, R42.2, U10.7
SINE2: C36.1, J3.7, R21.2, U10.1
SPI.CS: J2.1, R73.1, U12.1 (A4)
SQR1: J3.9, U2.6
SQR2: J3.10, U2.3
SQR3: J3.11, U2.8
SQR3_: C33.1, U2.9, U3.4 (RP56|RC8)
SQR4: J3.12, U2.11
SQR4_: C6.1, U2.12, U3.5 (RP57|RC9)
STAT: R52.1, U3.15 (RPI47|T5CK|RB15)
TxD2: J3.3, J6.7 (RXD), R57.2
VDDA: C17.1, C24.2, C39.1, C48.1, L1.1, R4.1, R12.2, R16.2, R18.1, R22.2, R23.1, R31.1, R32.2, R35.1, R36.2, R39.2, TP1.1, U3.17 (AVDD), U14.8 (VDD), U18.8 (VDD), U20.1 (Vdd)

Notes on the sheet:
Vout=1.23*210k/30k=8.61V
USB Connection Test Points BCu.
USB Port
Oscilloscope Channel 01
Power Source
Voltage Inverter Regulator
Real Time Clock Module
PWM Buffers
Battery Backup System
1.65V
Sine Wave Generator
Audio Channel
Circuit Protection
The AC Op-amp Integrator with DC Gain Control
Voltage Doubler
Vout=0.8*110k/10k=8.8V
I_chg = 100k * 1.2V / R_chg = 0.6A
USB to UART Bridge
1.50V
Miscellaneous
Oscilloscope Channel 03
Oscilloscope Channel 02
ESP-01 Expansion Slot
External Sockets

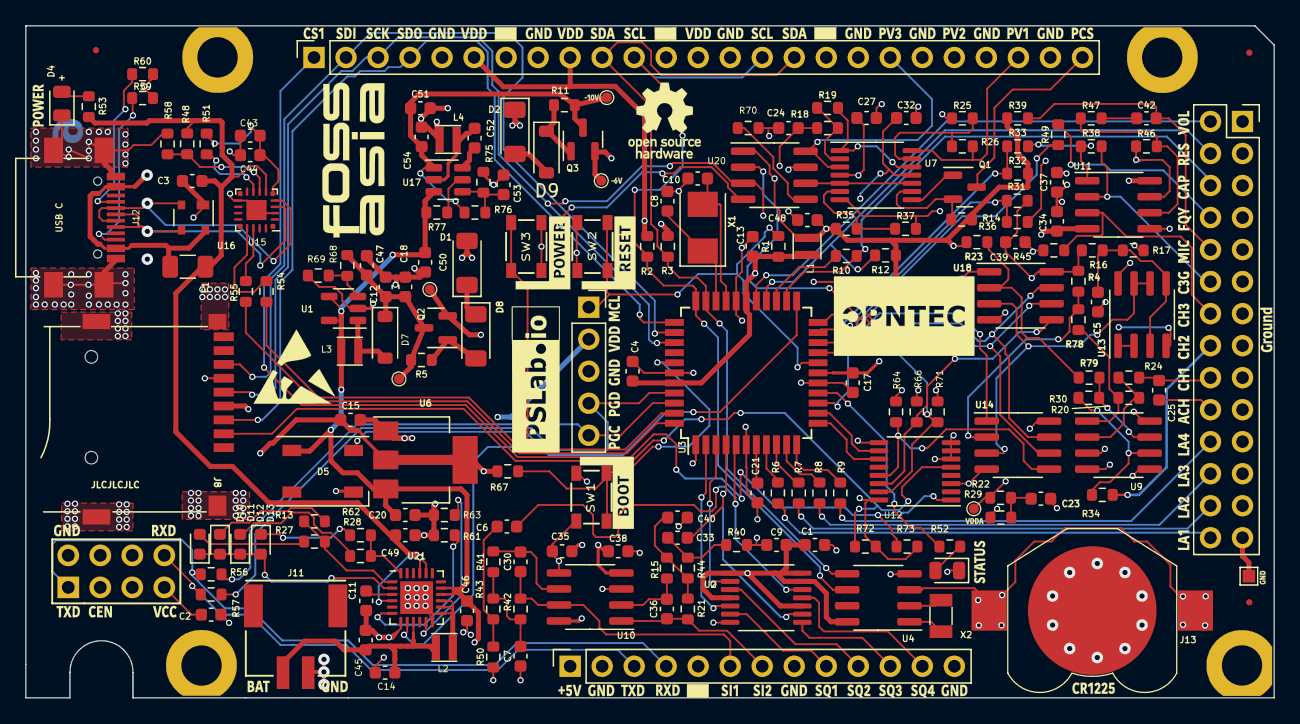
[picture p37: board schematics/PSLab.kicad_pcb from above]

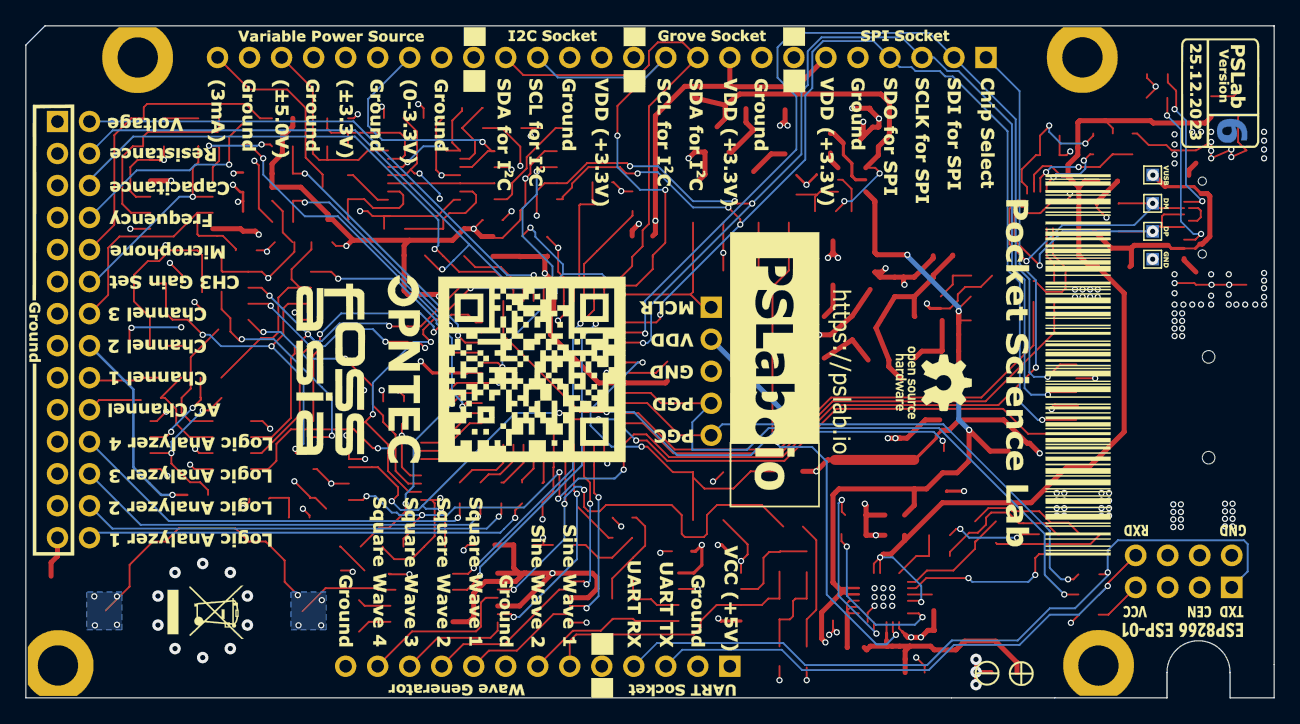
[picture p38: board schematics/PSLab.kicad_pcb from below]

Board: 4 copper layers, 99.0 x 53.3 mm, 199 parts (7 on the bottom side), 139 nets.

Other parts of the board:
Z11#2: OpenHardware; OSHW-Logo_5.7x6mm_SilkScreen

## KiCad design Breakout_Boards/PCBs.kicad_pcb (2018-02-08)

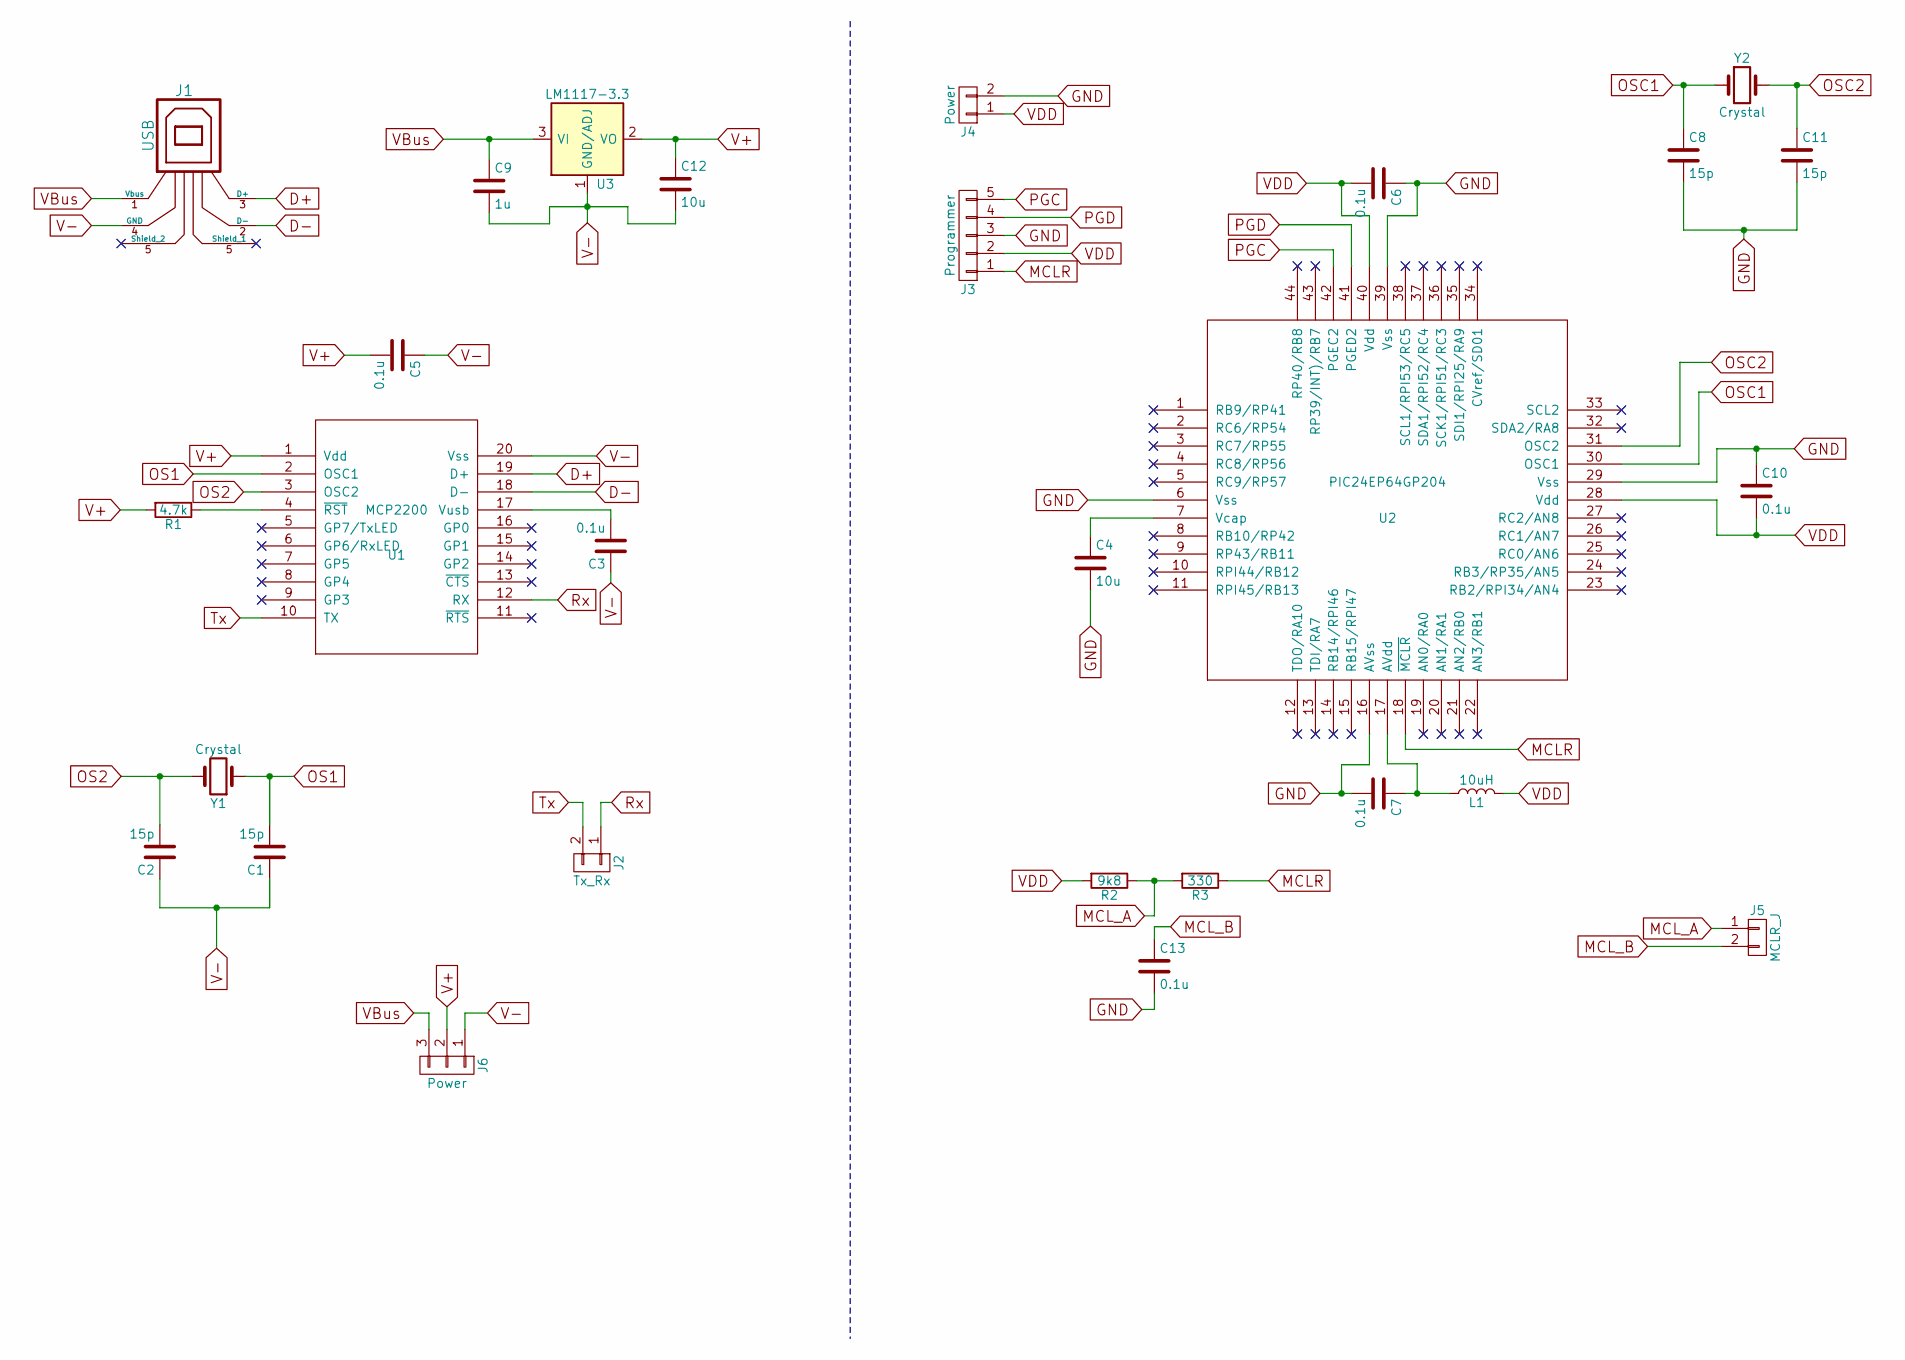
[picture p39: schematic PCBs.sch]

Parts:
C1, C2, C8, C11: 15p; C_0805_HandSoldering
C3, C5, C6, C7, C10, C13: 0.1u; C_0805_HandSoldering
C4, C12: 10u; C_0805_HandSoldering
C9: 1u; C_0805_HandSoldering
J1: USB; USB_B
J2: Tx_Rx; Pin_Header_Straight_1x02_Pitch2.54mm
J3: Programmer; Pin_Header_Straight_1x05_Pitch2.54mm
J4: Power; Pin_Header_Straight_1x02_Pitch2.54mm
J5: MCLR_J; Pin_Header_Straight_1x02_Pitch2.54mm
J6: Power; Pin_Header_Straight_1x03_Pitch2.54mm
L1: 10uH; L_0805_HandSoldering
R1: 4.7k; R_0805_HandSoldering
R2: 9k8; R_0805_HandSoldering
R3: 330; R_0805_HandSoldering
U1: MCP2200; SOIC-20W_7.5x12.8mm_Pitch1.27mm
U2: PIC24EP64GP204; TQFP-44_10x10mm_Pitch0.8mm
U3: LM1117-3.3; SOT-223
Y1, Y2: Crystal; Crystal_HC49-4H_Vertical

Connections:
D+: J1.3 (D+), U1.19 (D+)
D-: J1.2 (D-), U1.18 (D-)
GND: C4.2, C6.1, C7.2, C8.2, C10.1, C11.2, C13.2, J3.3, J4.2, U2.6 (Vss), U2.16 (AVss), U2.29 (Vss), U2.39 (Vss)
MCLR: J3.1, R3.1, U2.18 (~MCLR)
MCL_A: J5.1, R2.1, R3.2
MCL_B: C13.1, J5.2
unnamed: C3.2, U1.17 (Vusb)
unnamed: C4.1, U2.7 (Vcap)
unnamed: C7.1, L1.1, U2.17 (AVdd)
unnamed: R1.1, U1.4 (~RST)
OS1: C1.2, U1.2 (OSC1), Y1.1
OS2: C2.2, U1.3 (OSC2), Y1.2
OSC1: C8.1, U2.30 (OSC1), Y2.1
OSC2: C11.1, U2.31 (OSC2), Y2.2
PGC: J3.5, U2.42 (PGEC2)
PGD: J3.4, U2.41 (PGED2)
Rx: J2.1, U1.12 (RX)
Tx: J2.2, U1.10 (TX)
V+: C5.2, C12.1, J6.2, R1.2, U1.1 (Vdd), U3.2 (VO), U3.4 (VO)
V-: C1.1, C2.1, C3.1, C5.1, C9.2, C12.2, J1.4 (GND), J6.1, U1.20 (Vss), U3.1 (GND/ADJ)
VBus: C9.1, J1.1 (Vbus), J6.3, U3.3 (VI)
VDD: C6.2, C10.2, J3.2, J4.1, L1.2, R2.2, U2.28 (Vdd), U2.40 (Vdd)

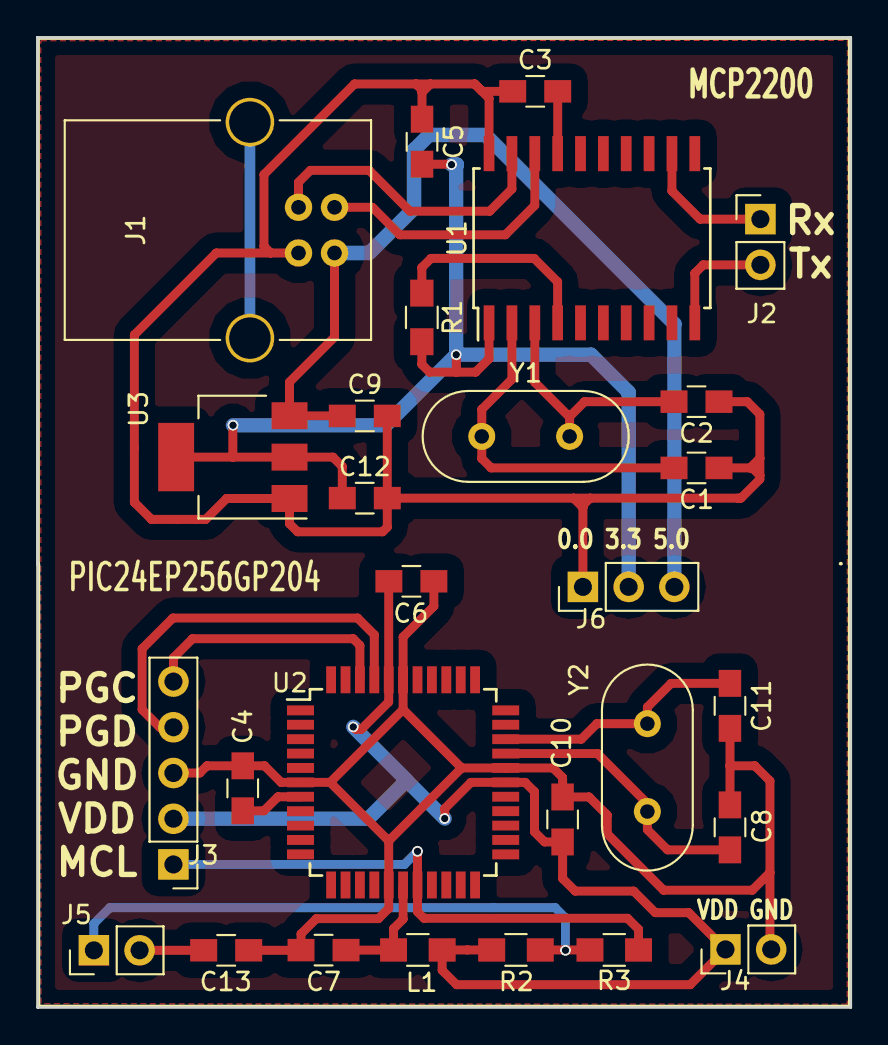
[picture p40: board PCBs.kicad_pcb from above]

Board: 2 copper layers, 45.2 x 53.9 mm, 28 parts (0 on the bottom side), 22 nets.

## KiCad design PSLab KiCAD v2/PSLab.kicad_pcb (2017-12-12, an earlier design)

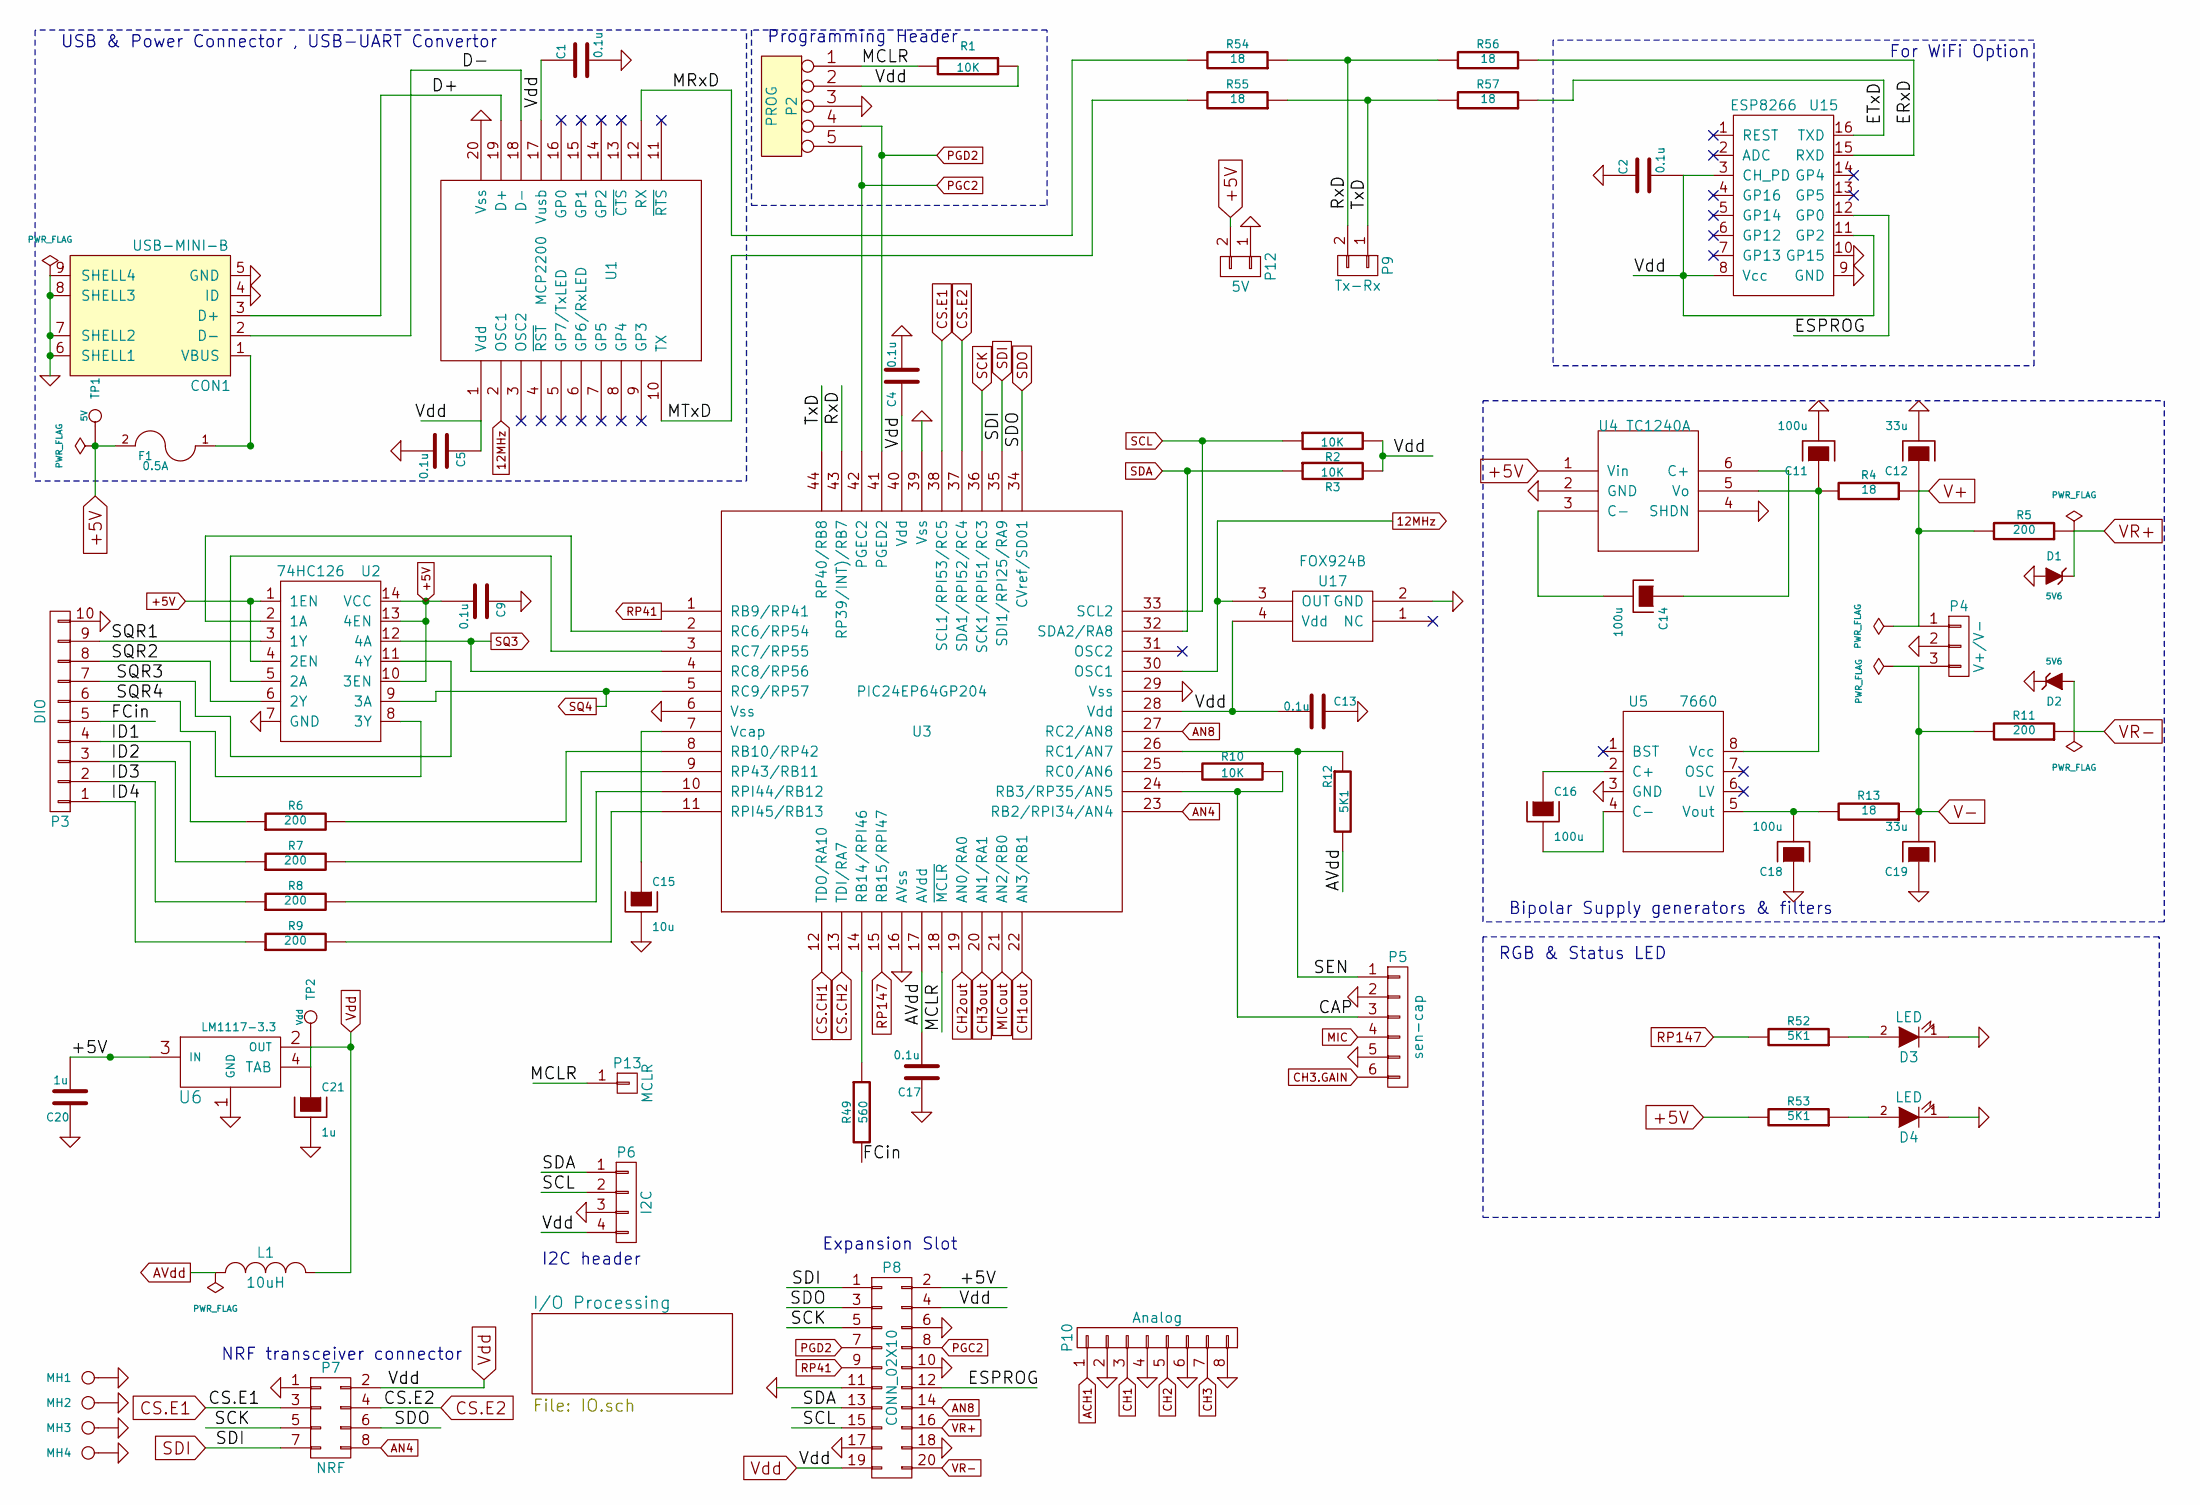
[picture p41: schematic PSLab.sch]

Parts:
C1, C2, C4, C5, C9, C13, C17: 0.1u; C_0805
C11, C14, C16, C18: 100u; TantalC_SizeC_EIA-6032_Reflow
C12, C19: 33u; myTantalC_SizeA
C15: 10u; C_0805
C20, C21: 1u; C_0805
CON1: USB-MINI-B; myUSB_MINI_B-special
D1, D2: 5V6; Diode-MiniMELF_Standard
D3: LED; myPin_Header_Straight_1x02
D4: LED; C_0805
F1: 0.5A; Fuse_SMD1206_Reflow
L1: 10uH; C_0805
MH1, MH2, MH3, MH4: M; MountingHole-clear
P2: PROG; myPin_Header_Straight_1x05-no3D
P3: DIO; Pin_Header_Straight_1x10
P4: V+/V-; mySocket_3x1
P5: sen-cap; myPin_Header_Straight_1x06-oval
P6: I2C; Socket_Strip_Straight_1x04
P7: NRF; NRF24-noborder
P8: CONN_02X10; MYPin_Header_Straight_2x10
P9: Tx-Rx; myPin_Header_Straight_1x02
P10: Analog; myPin_Header_Straight_1x08-oval
P12: 5V; myPin_Header_Straight_1x02
P13: MCLR; pad
R1, R2, R3, R10: 10K; R_0805
R4, R13, R54, R55, R56, R57: 18; R_0805
R5, R6, R7, R8, R9, R11: 200; R_0805
R12, R52, R53: 5K1; R_0805
R49: 560; R_0805
TP1: 5V; myTestPoint
TP2: Vdd; myTestPoint
U1: MCP2200; SOIC-20-W
U2: 74HC126; SOIC-14_N
U3: PIC24EP64GP204; TQFP-44
U4: TC1240A; SOT-23-6
U5: 7660; SOIC-8-N
U6: LM1117-3.3; SOT-223
U15: ESP8266; ESP12
U17: FOX924B; Crystal_SMD_EuroQuartz_MJ-4pin_5.0x3.2mm

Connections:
12MHz: U1.2 (OSC1), U3.30 (OSC1), U17.3 (OUT)
+5V: C9.2, C20.2, F1.2, P8.2, P12.2, R53.2, TP1.1, U2.1 (1EN), U2.4 (2EN), U2.10 (3EN), U2.13 (4EN), U2.14 (VCC), U4.1 (Vin), U6.3 (IN); also elsewhere on the board
/CAP: P5.3, R10.1, U3.24 (RB3/RP35/AN5)
/D+: CON1.3 (D+), U1.19 (D+)
/D-: CON1.2 (D-), U1.18 (D-)
/ERxD: R56.1, U15.15 (RXD)
/ESPROG: P8.12, U15.12 (GP0)
/ETxD: R57.1, U15.16 (TXD)
/FCin: P3.5, R49.2; also elsewhere on the board
/ID1: P3.4, R6.1
/ID2: P3.3, R7.1
/ID3: P3.2, R8.1
/ID4: P3.1, R9.1
/MCLR: P2.1, P13.1, R1.2, U3.18 (~MCLR)
/MRxD: R54.2, U1.12 (RX)
/MTxD: R55.2, U1.10 (TX)
/RxD: P9.2, R54.1, R56.2, U3.43 (RP39/INT)/RB7)
/SEN: P5.1, R12.1, U3.26 (RC1/AN7)
/SQR1: P3.9, U2.3 (1Y)
/SQR2: P3.8, U2.6 (2Y)
/SQR3: P3.7, U2.11 (4Y)
/SQR4: P3.6, U2.8 (3Y)
/TxD: P9.1, R55.1, R57.2, U3.44 (RP40/RB8)
ACH1: P10.1; also elsewhere on the board
AN4: P7.8, U3.23 (RB2/RPI34/AN4)
AN8: P8.14, U3.27 (RC2/AN8)
AVdd: C17.2, L1.1, R12.2, U3.17 (AVdd); also elsewhere on the board
CH1: P10.3; also elsewhere on the board
CH1out: U3.22 (AN3/RB1); also elsewhere on the board
CH2: P10.5; also elsewhere on the board
CH2out: U3.19 (AN0/RA0); also elsewhere on the board
CH3: P10.7; also elsewhere on the board
CH3.GAIN: P5.6; also elsewhere on the board
CH3out: U3.20 (AN1/RA1); also elsewhere on the board
CS.CH1: U3.12 (TDO/RA10); also elsewhere on the board
CS.CH2: U3.13 (TDI/RA7); also elsewhere on the board
CS.E1: P7.3, U3.38 (SCL1/RPI53/RC5)
CS.E2: P7.4, U3.37 (SDA1/RPI52/RC4)
MIC: P5.4; also elsewhere on the board
MICout: U3.21 (AN2/RB0); also elsewhere on the board
unnamed: C11.1, R4.2, U4.5 (Vo), U5.8 (Vcc)
unnamed: C14.1, U4.6 (C+)
unnamed: C14.2, U4.3 (C-)
unnamed: C15.1, U3.7 (Vcap)
unnamed: C16.1, U5.2 (C+)
unnamed: C16.2, U5.4 (C-)
unnamed: C18.2, R13.2, U5.5 (Vout)
unnamed: CON1.1 (VBUS), F1.1
unnamed: D3.2 (A), R52.1
unnamed: D4.2 (A), R53.1
unnamed: R6.2, U3.8 (RB10/RP42)
unnamed: R7.2, U3.9 (RP43/RB11)
unnamed: R8.2, U3.10 (RPI44/RB12)
unnamed: R9.2, U3.11 (RPI45/RB13)
unnamed: R10.2, U3.25 (RC0/AN6)
unnamed: R49.1, U3.14 (RB14/RPI46)
unnamed: U2.2 (1A), U3.2 (RC6/RP54)
unnamed: U2.5 (2A), U3.3 (RC7/RP55)
PGC2: P2.5, P8.8, U3.42 (PGEC2)
PGD2: P2.4, P8.7, U3.41 (PGED2)
RP41: P8.9, U3.1 (RB9/RP41)
RP147: R52.2, U3.15 (RB15/RPI47)
SCK: P7.5, P8.5, U3.36 (SCK1/RPI51/RC3); also elsewhere on the board
SCL: P6.2, P8.15, R2.1, U3.33 (SCL2); also elsewhere on the board
SDA: P6.1, P8.13, R3.1, U3.32 (SDA2/RA8); also elsewhere on the board
SDI: P7.7, P8.1, U3.35 (SDI1/RPI25/RA9)
SDO: P7.6, P8.3, U3.34 (CVref/SD01); also elsewhere on the board
SQ3: U2.12 (4A), U3.4 (RC8/RP56); also elsewhere on the board
SQ4: U2.9 (3A), U3.5 (RC9/RP57); also elsewhere on the board
V+: C12.1, P4.1, R4.1, R5.2; also elsewhere on the board
V-: C19.2, P4.3, R11.2, R13.1; also elsewhere on the board
VR+: D1.2 (K), P8.16, R5.1; also elsewhere on the board
VR-: D2.1 (A), P8.20, R11.1; also elsewhere on the board
Vdd: C1.1, C2.2, C4.1, C5.1, C13.2, C21.1, L1.2, P2.2, P6.4, P7.2, P8.4, P8.19, R1.1, R2.2, R3.2, TP2.1, U1.1 (Vdd), U1.17 (Vusb), U3.28 (Vdd), U3.40 (Vdd), U6.2 (OUT), U6.4 (TAB), U15.3 (CH_PD), U15.8 (Vcc), U15.11 (GP2), U17.4 (Vdd)

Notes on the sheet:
For WiFi Option
USB & Power Connector , USB-UART Convertor
Programming Header
Bipolar Supply generators & filters
RGB & Status LED
I2C header
NRF transceiver connector
Expansion Slot

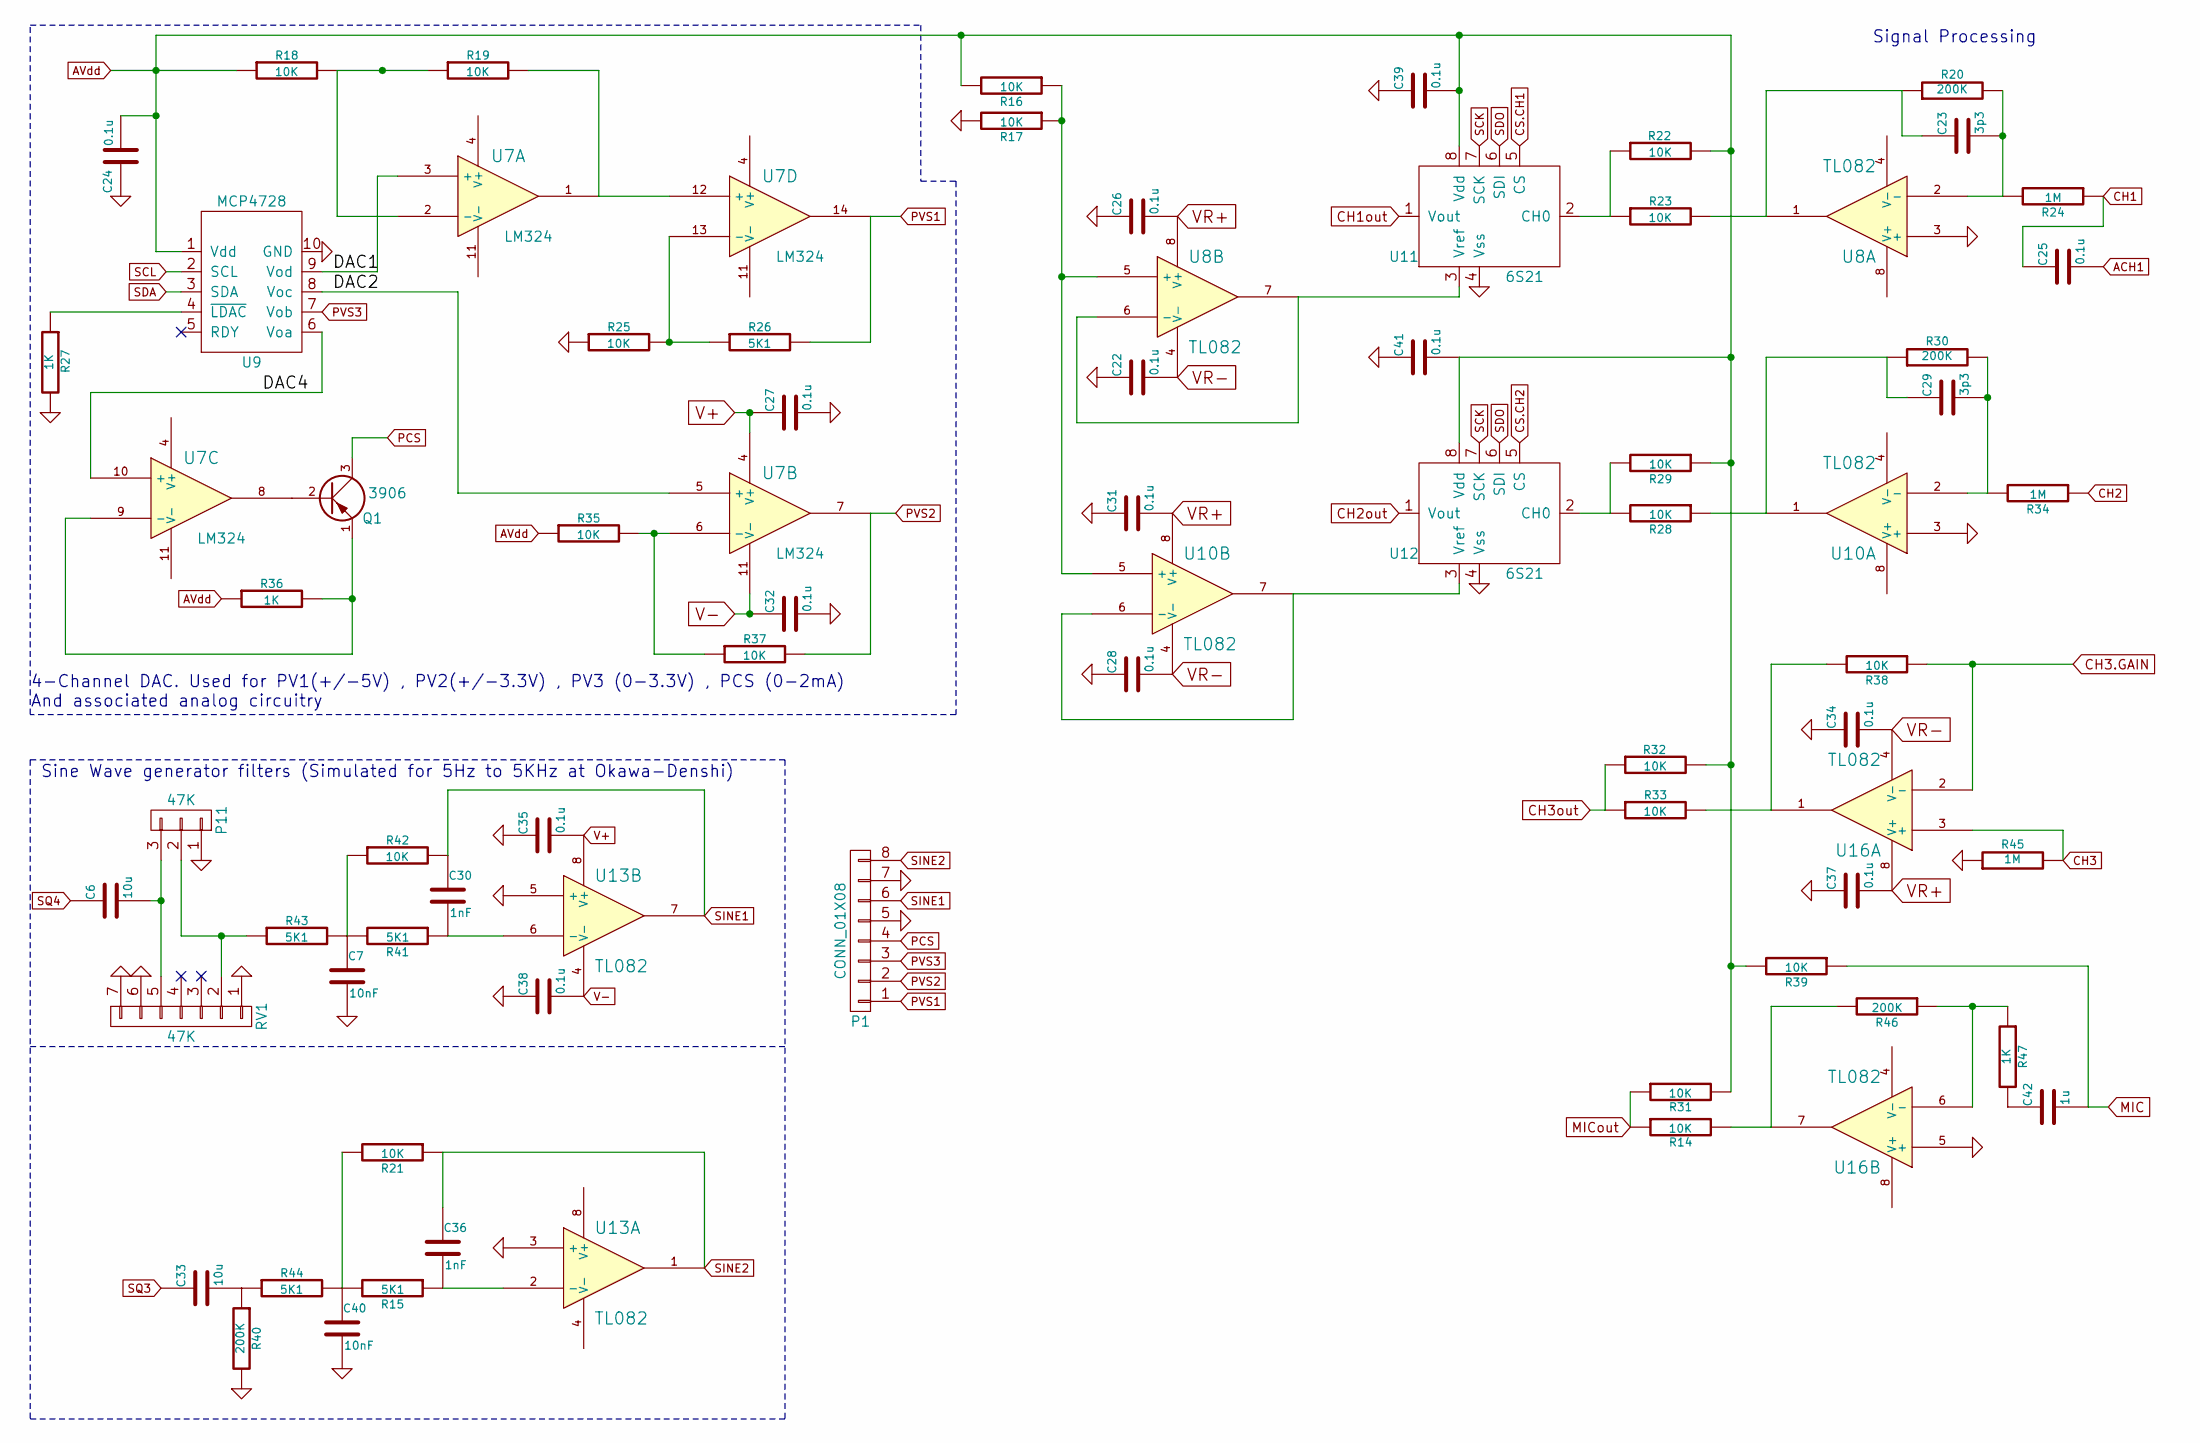
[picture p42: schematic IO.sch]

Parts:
C6, C33: 10u; C_0805
C7, C40: 10nF; C_0805
C22, C24, C25, C26, C27, C28, C31, C32, C34, C35, C37, C38, C39, C41: 0.1u; C_0805
C23, C29: 3p3; C_0805
C30, C36: 1nF; C_0805
C43: 1u; C_0805
P1: CONN_01X08; myPin_Header_Straight_1x08-oval
P11: 47K; slider-3-socket
Q1: 3906; SOT-23-EBC
R14, R16, R17, R18, R19, R21, R22, R23, R25, R28, R29, R31, R32, R33, R35, R37, R38, R39, R42: 10K; R_0805
R15, R26, R41, R43, R44: 5K1; R_0805
R20, R30, R40, R46: 200K; R_0805
R24, R34, R45: 1M; R_0805
R27, R36, R47: 1K; R_0805
RV1: 47K; slider-pot-new
U7: LM324; SOIC-14_N
U8, U10, U13, U16: TL082; SOIC-8-N
U9: MCP4728; MSOP-10-0.5mm-hand
U11, U12: 6S21; SOIC-8-N

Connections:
/I/O Processing/DAC1: U7.3 (+), U9.9 (Vod)
/I/O Processing/DAC2: U7.5 (+), U9.8 (Voc)
/I/O Processing/DAC4: U7.10 (+), U9.6 (Voa)
ACH1: C25.2; also elsewhere on the board
AVdd: C24.2, C39.2, C41.2, R16.2, R18.1, R22.2, R29.1, R31.2, R32.2, R35.1, R36.1, R39.2, U9.1 (Vdd), U11.8 (Vdd), U12.8 (Vdd); also elsewhere on the board
CH1: C25.1, R24.1; also elsewhere on the board
CH1out: U11.1 (Vout); also elsewhere on the board
CH2: R34.1; also elsewhere on the board
CH2out: U12.1 (Vout); also elsewhere on the board
CH3: R45.2, U16.3 (+); also elsewhere on the board
CH3.GAIN: R38.1, U16.2 (-); also elsewhere on the board
CH3out: R32.1, R33.1; also elsewhere on the board
CS.CH1: U11.5 (CS); also elsewhere on the board
CS.CH2: U12.5 (CS); also elsewhere on the board
MIC: R39.1; also elsewhere on the board
MICout: R14.1, R31.1; also elsewhere on the board
unnamed: C6.2, P11.3, RV1.5
unnamed: C7.1, R41.2, R42.1, R43.2
unnamed: C23.1, R20.1, R23.2, U8.1
unnamed: C23.2, R20.2, R24.2, U8.2 (-)
unnamed: C29.1, R28.1, R30.1, U10.1
unnamed: C29.2, R30.2, R34.2, U10.2 (-)
unnamed: C30.2, R41.1, U13.6 (-)
unnamed: C33.2, R40.1, R44.1
unnamed: C36.2, R15.1, U13.2 (-)
unnamed: C40.1, R15.2, R21.2, R44.2
unnamed 62: R47.2; also elsewhere on the board
unnamed: P11.2, R43.1, RV1.2
unnamed: Q1.1 (E), R36.2, U7.9 (-)
unnamed: Q1.2 (B), U7.8
unnamed: R14.2, R46.2, U16.7
unnamed: R16.1, R17.1, U8.5 (+), U10.5 (+)
unnamed: R18.2, R19.1, U7.2 (-)
unnamed: R19.2, U7.1, U7.12 (+)
unnamed: R22.1, R23.1, U11.2 (CH0)
unnamed: R25.2, R26.1, U7.13 (-)
unnamed: R27.1, U9.4 (~LDAC)
unnamed: R28.2, R29.2, U12.2 (CH0)
unnamed: R33.2, R38.2, U16.1
unnamed: R35.2, R37.1, U7.6 (-)
unnamed: R46.1, R47.1, U16.6 (-)
unnamed: U10.6 (-), U10.7, U12.3 (Vref)
unnamed: U8.6 (-), U8.7, U11.3 (Vref)
PCS: P1.4, Q1.3 (C)
PVS1: P1.1, R26.2, U7.14
PVS2: P1.2, R37.2, U7.7
PVS3: P1.3, U9.7 (Vob)
SCK: U11.7 (SCK), U12.7 (SCK); also elsewhere on the board
SCL: U9.2 (SCL); also elsewhere on the board
SDA: U9.3 (SDA); also elsewhere on the board
SDO: U11.6 (SDI), U12.6 (SDI); also elsewhere on the board
SINE1: C30.1, P1.6, R42.2, U13.7
SINE2: C36.1, P1.8, R21.1, U13.1
SQ3: C33.1; also elsewhere on the board
SQ4: C6.1; also elsewhere on the board
V+: C27.1, C35.2, U7.4 (V+), U13.8 (V+); also elsewhere on the board
V-: C32.1, C38.2, U7.11 (V-), U13.4 (V-); also elsewhere on the board
VR+: C26.2, C31.2, C37.2, U8.8 (V+), U10.8 (V+), U16.8 (V+); also elsewhere on the board
VR-: C22.2, C28.2, C34.2, U8.4 (V-), U10.4 (V-), U16.4 (V-); also elsewhere on the board

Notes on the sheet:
4-Channel DAC. Used for PV1(+/-5V) , PV2(+/-3.3V) , PV3 (0-3.3V) , PCS (0-2mA) And associated analog circuitry
Sine Wave generator filters (Simulated for 5Hz to 5KHz at Okawa-Denshi)
Signal Processing

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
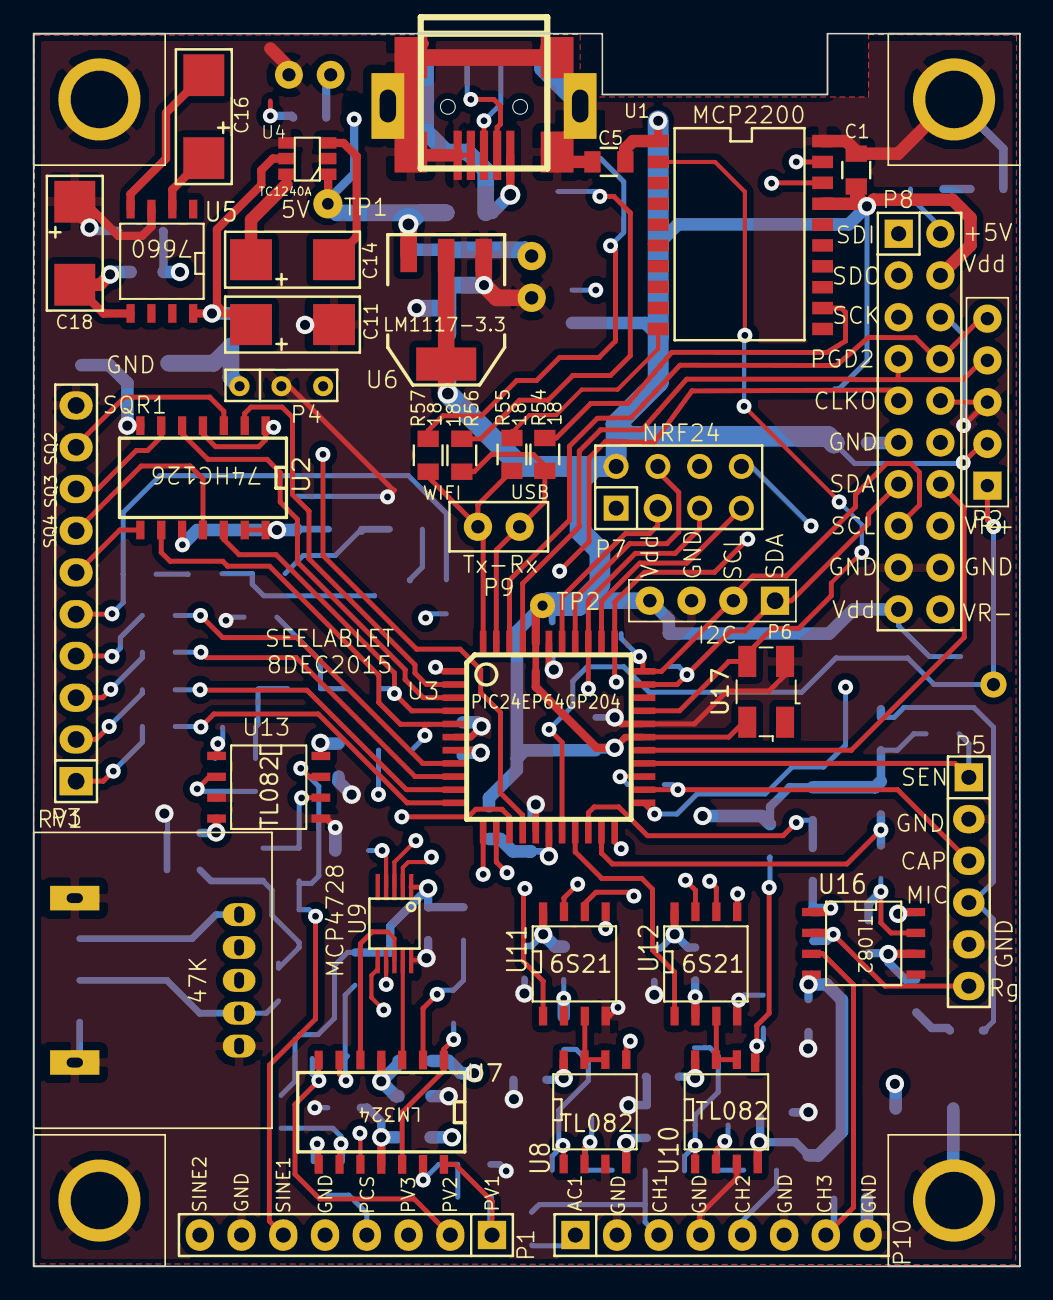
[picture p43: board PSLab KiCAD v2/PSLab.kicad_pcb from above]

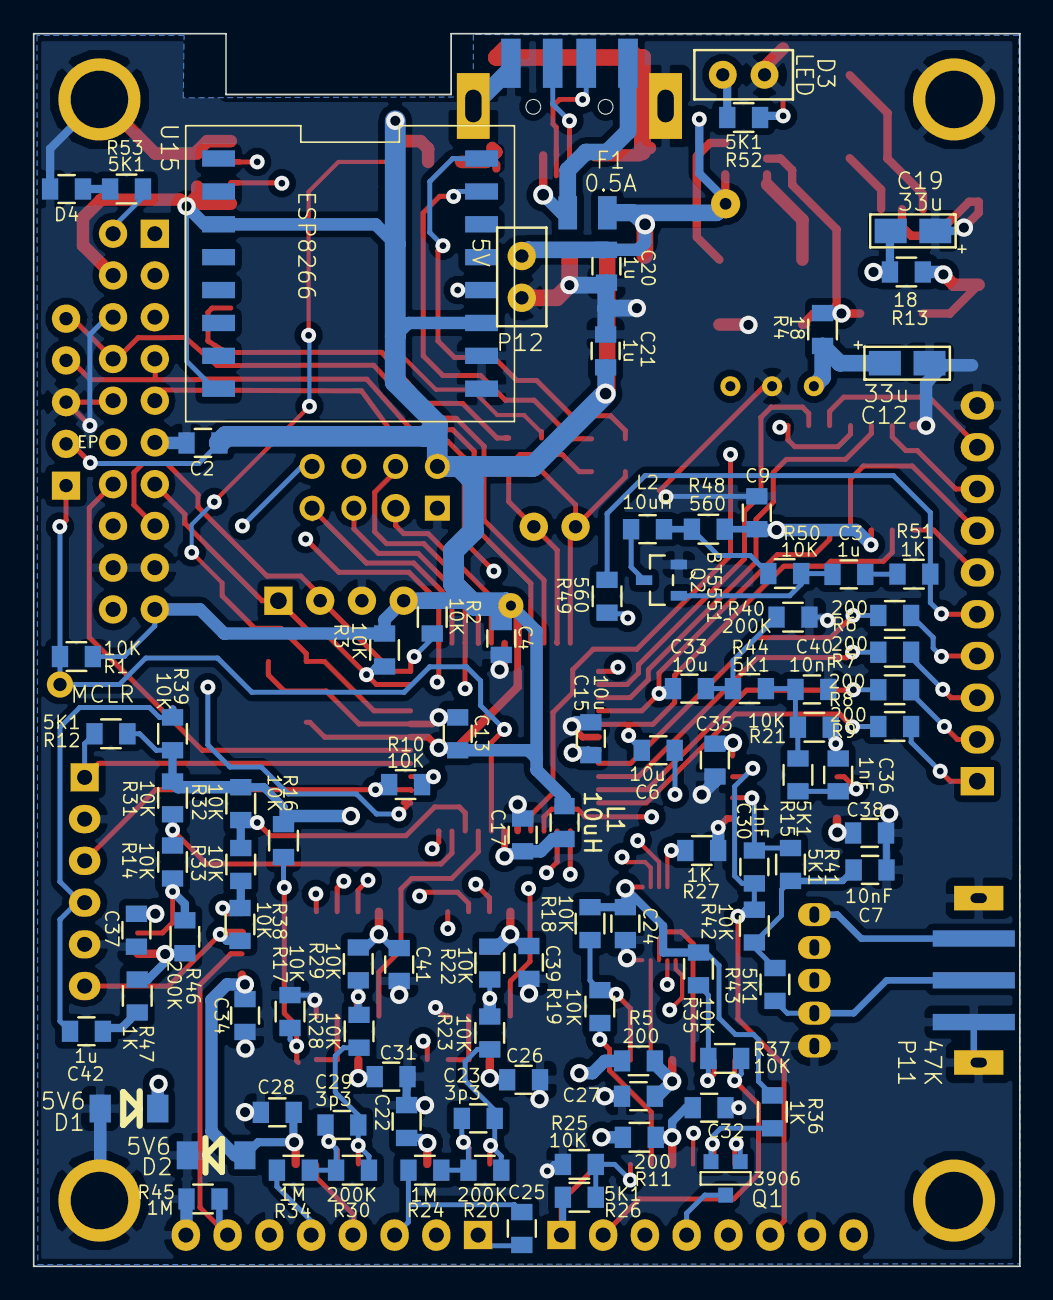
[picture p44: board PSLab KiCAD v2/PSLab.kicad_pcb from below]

Board: 4 copper layers, 60.0 x 75.0 mm, 143 parts (100 on the bottom side), 115 nets.

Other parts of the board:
C3, C42: 1u; C_0805
L2: 10uH; C_0805
Q2: BT5551; sot23
R48: 560; R_0805
R50: 10K; R_0805
R51: 1K; R_0805

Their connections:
+5V: R48.1; also elsewhere on the board
/FCin: R51.1; also elsewhere on the board
MIC: C42.2; also elsewhere on the board
unnamed: C3.1, Q2.1, R50.2
unnamed: C3.2, R51.2
unnamed 62: C42.1; also elsewhere on the board
unnamed: L2.1, Q2.3
unnamed: L2.2, R48.2, R50.1

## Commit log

2017-04-02 KiCAD project inc schematics. layout remaining
    [IO.sch, PERIPHERALS.sch, PSLab.sch]
2017-04-13 add netlist & layout files
    [PSLab.kicad_pcb]
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2017-06-08 Added SMD Crystal replacing through hole Oscillator (#12)
    * Added SMD Crystal replacing through hole Oscillator
    * Fixed Electric rules
    * Removed extra 15pF capacitor
    * Added gitignore
    [IO.sch, PERIPHERALS.sch, PSLab.kicad_pcb, PSLab.sch]
2017-07-06 DRC errors fixed in pcb layout (#18)
    [PSLab.kicad_pcb]
2017-12-09 Fix #19: Removed redundant LED foot print
    [IO.sch, PSLab.kicad_pcb, PSLab.sch]
2017-12-11 Fix #21 : Transform current board to Uno compatible board
    Routing in progress
    Placed components inside board
    All connections complete
    Have to optimize
    Modifications to the schematics
    [IO.sch, PERIPHERALS.sch, PSLab.kicad_pcb, PSLab.sch]
2017-12-12 Labeling the PCB
    [PSLab.kicad_pcb]
2017-12-12 Adding zones
    [PSLab.kicad_pcb]
2017-12-25 Fixes #23 : Replaced USB port with USB Micro B type (#24)
    [PSLab.kicad_pcb, PSLab.sch]
2018-01-08 Fixes #25 : Added BoM and Gerber files for production (#26)
    * Fixes #23 : Replaced USB port with USB Micro B type
    * Added Gerber files
    [IO.sch, PSLab-B.Cu-L4.gbl, PSLab-B.Mask.gbs, PSLab-B.SilkS.gbo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]
2018-01-11 Fixes #27 : Replaced microcontroller (#28)
    [PSLab.kicad_pcb, PSLab.sch]
2018-01-20 Fixes #30 : Transfered components to top side (#31)
    * Fixes #30 : Transfered components to top side
    * Optimizing layout
    * Added updated schematics PDF
    * Fixing Travis
    * Programmer pin header adjustments
    [IO.sch, PERIPHERALS.sch, PSLab.kicad_pcb, PSLab.sch]
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2018-01-21 Ran DRC Check on layout
    [PSLab.kicad_pcb]
2018-01-23 Added Gerber files
    [IO.sch, PSLab-B.Cu-L4.gbl, PSLab-B.Mask.gbs, PSLab-B.SilkS.gbo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]
2018-02-08 Added breakouts for MCP2200 & PIC24 (#36)
    * Added breakouts for MCP2200
    * Added guard rings for OSC
    * Grounded mount holes
    * Gerber files updated
    [IO.sch, PCBs-B.Cu.gbl, PCBs-B.Mask.gbs, PCBs-B.Paste.gbp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]
2018-02-14 Updated docs with new layout
    [IO.sch, PSLab-B.Cu-L4.gbl, PSLab-B.Mask.gbs, PSLab-B.Paste.gbp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]
2018-04-19 New layout with pins adjusted + Bluetooth
    [IO.sch, PSLab-B.Cu-L4.gbl, PSLab-B.Mask.gbs, PSLab-B.Paste.gbp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]
2018-04-19 Added Gerber files for new layout
    [PSLab-B.Cu-L4.gbl, PSLab-B.Mask.gbs, PSLab-B.Paste.gbp, PSLab-B.SilkS.gbo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]
2018-05-11 Modifications to PSLab PCB (#39)
    * Refined BOM Sheet
    * Added FOSSASIA Logo and updated BoM
    * NRF replaced with Bluetooth
    * Modified silk screen texts
    [IO.sch, PSLab-B.Cu-L4.dxf, PSLab-B.Cu-L4.gbl, PSLab-B.Mask.dxf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]
2018-06-10 fix: updated pin layout diagram (#44)
    added v4 pin layout
    added missing GND pin
    added pslabdesign.png
    enhanced kicad fossasia logo
    [PSLab-B.Cu-L4.gbl, PSLab-B.Mask.gbs, PSLab-B.Paste.gbp, PSLab-B.SilkS.gbo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]
2018-06-10 fix: archive old versions (#43)
    updated docs folder
    [IO.sch, PCBs-B.Cu.gbl, PCBs-B.Mask.gbs, PCBs-B.Paste.gbp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]
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2018-08-22 feat: added fiducial marks
    [PSLab-B.Cu-L4.gbl, PSLab-B.Mask.gbs, PSLab-B.Paste.gbp, PSLab-B.SilkS.gbo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]
2018-09-05 feat: centroid file for automatic placement
    gerber zip
    [PSLab-B.Cu-L4.dxf, PSLab-B.Cu-L4.gbl, PSLab-B.Mask.dxf, PSLab-B.Mask.gbs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]
2018-09-08 added logos and barcodes
    [PSLab-B.Cu-L4.gbl, PSLab-B.Mask.gbs, PSLab-B.Paste.gbp, PSLab-B.SilkS.gbo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]
2018-09-09 barcode update (#56)
    [PSLab-B.Cu-L4.gbl, PSLab-B.Mask.gbs, PSLab-B.Paste.gbp, PSLab-B.SilkS.gbo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]
2018-09-11 updated pad sizes (#57)
    [PSLab-B.Cu-L4.gbl, PSLab-B.Mask.gbs, PSLab-B.Paste.gbp, PSLab-B.SilkS.gbo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]
2018-09-12 updated pads to M2.5
    [PSLab-B.Cu-L4.gbl, PSLab-B.Mask.gbs, PSLab-B.Paste.gbp, PSLab-B.SilkS.gbo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]
2018-09-20 added dxf files
    [PSLab-B.Adhes.dxf, PSLab-B.Cu-L4.dxf, PSLab-B.Mask.dxf, PSLab-B.Paste.dxf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]
2018-09-25 Updated BoM with nuts
    file reorder
    pos correction
    updated dxfs
    [PSLab-F.Cu-L1.dxf, PSLab-F.Mask.dxf, PSLab-F.Paste.dxf, PSLab-drl_map.dxf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]
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2018-11-04 fix: updated design with revised changes
    Fixes #70 #66 #63 #62 #61
    updated
    updated images
    updated folders
    [PSLab-B.Adhes.dxf, PSLab-B.Cu-L4.dxf, PSLab-B.Cu-L4.gbl, PSLab-B.Mask.dxf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]
2018-11-05 feat: added version numbers
    [PSLab-B.Adhes.dxf, PSLab-B.Cu-L4.dxf, PSLab-B.Cu-L4.gbl, PSLab-B.Mask.dxf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]
2018-12-09 feat: added drawings (#77)
    [PSLabFront.dwg, PSLabUpper.dwg]
2018-12-09 docs: added dxf and svg formats (#78)
    [IO.sch, PSLabFront.dxf, PSLabUpper.dxf]
2018-12-22 feat: M3 Nuts and M3.5 Standoffs
    [PSLab-B.Cu-L4.dxf, PSLab-B.Cu-L4.gbl, PSLab-B.Mask.dxf, PSLab-B.Mask.gbs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]
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2018-12-30 fix: updated BoM with latest tolerance levels
    [PSLab_BOM_Sheet.ods]
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2019-03-07 board: switch to latest KiCAD version
    route: fix switch routes
    fix: DRC Issues fixed
    docs: added new schematics PDF
    docs: updated BoM for v6 PSLab
    [IO-2019-03-02-11-42-31.sch, Logos-2019-03-02-11-42-31.sch, PSLab-2019-03-02-11-42-31.sch, PSLab.kicad_pcb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]
2019-03-07 feat: 3D models with new KiCAD version
    route: VDD missing routes being fixed
    route: UART routes
    route: complete
    3D footprints and optimization
    [PSLab.kicad_pcb]
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2019-03-31 PSLab V6 (#93)
    * board: component placement in v6
    * board: switch to latest KiCAD version
    * feat: 3D models with new KiCAD version
    * route: optimization
    * docs: updated BoM
    * update: added spacing with more test points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
    [IO-2019-03-02-11-42-31.sch, IO.sch, Logos-2019-03-02-11-42-31.sch, Logos.sch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]
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2020-03-15 fix: edge endpoints
    [PSLab.kicad_pcb]
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2020-05-16 fix: routing errors and layout issues
    [PSLab-B_Adhes.dxf, PSLab-B_Mask.dxf, PSLab-B_Mask.gbs, PSLab-B_Paste.dxf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]
2020-05-16 fix: placement
    [PSLab.kicad_pcb]
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2020-08-27 fix: drill origin set away from board
    [PSLab-B_Mask.gbs, PSLab-B_Paste.gbp, PSLab-B_SilkS.gbo, PSLab-F_Mask.dxf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]
2020-08-27 fix: increased cutoff frequency
    [IO.sch, PSLab.kicad_pcb]
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2020-08-27 fix: updated bom with correct footprints
    [PSLab-B_Mask.gbs, PSLab-B_Paste.gbp, PSLab-B_SilkS.gbo, PSLab-Edge_Cuts.gm1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]
2020-10-21 fix: position correction for production
    [PSLab-B_Mask.gbs, PSLab-B_Paste.gbp, PSLab-B_SilkS.gbo, PSLab-Edge_Cuts.gm1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]
2020-10-21 fix: fiducials for production
    [PSLab-B_Mask.gbs, PSLab-B_Paste.gbp, PSLab-B_SilkS.gbo, PSLab-Edge_Cuts.gm1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]
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2020-10-21 fix: line issues in uart ic for external power
    [PSLab-B_Mask.gbs, PSLab-B_Paste.gbp, PSLab-B_SilkS.gbo, PSLab-Edge_Cuts.gm1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]
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2020-10-21 refactor: fixed rotation in resistors
    [IO.sch, PSLab.kicad_pcb, PSLab.sch, UARTBridge.sch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]
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2020-10-24 fix: courtyars, F2 fuse and RGB LED diode
    [Logos.sch, PSLab-B_Mask.gbs, PSLab-B_Paste.gbp, PSLab-B_SilkS.gbo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]
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2020-10-24 refactor: corrected IC annotation order
    [IO.sch, PSLab-B_Mask.gbs, PSLab-B_Paste.gbp, PSLab-B_SilkS.gbo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]
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2020-10-25 fix: USB C at bottom, gerber files in .gbr
    [PSLab-B_Mask.gbr, PSLab-B_Paste.gbp, PSLab-B_Paste.gbr, PSLab-B_SilkS.gbr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]
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2021-04-12 refactor: fixing i2c lines
    [PSLab.kicad_pcb]
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2021-05-26 fix: doc-lib for components
    [BillOfMaterials.csv, PSLab.drl, PSLab.gbr, PSLab.gbrjob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]
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2021-06-03 fix: osc signal routes
    [HC05.STEP, PSLab.kicad_pcb, PSLab.sch]
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2021-07-01 fix: resistor placement to optimize routing
    [PSLab.kicad_pcb, PSLab.sch]
2021-07-08 feat: updated USB C port and fixed LTC4040 SW connection
    [PSLab.kicad_pcb, PSLab.sch, TYPE-C-31-M-12.step, USBCPort.STEP]
2021-07-08 fix: wavegen and i2c routes
    [PSLab.kicad_pcb, PSLab.sch]
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2021-07-08 fix: high power lines
    [PSLab.kicad_pcb, PSLab.sch]
2021-07-08 fix: power routes
    [PSLab.kicad_pcb]
2021-07-09 fix: usb power routes
    [PSLab.kicad_pcb]
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2021-08-06 fix: updated silk screen at U1
    [PSLab.kicad_pcb]
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2021-10-20 fix: ESP Pinout Labeling
    [BillOfMaterials.csv, PSLab-B_Mask.gbr, PSLab-B_Paste.gbr, PSLab-B_SilkS.gbr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]
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2023-01-20 refactor: replace LTC4040 with IP5189T
    [PSLab.sch]
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2023-01-20 chore: replace switch to SPST_3x4x2.5
    [PSLab.sch]
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2023-01-20 refactor: replace PGA MAX6S21 with TL082 and MAX5400, modify PCB
    [PSLab.sch]
2023-01-20 refactor: replace MCP4728 with 2 MPC4822
    [PSLab.sch]
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2023-01-20 refactor: replace IP5189T to IP5219T
    [PSLab.sch]
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2023-01-20 refactor: replace IP5219 to IP51289T
    [PSLab.sch]
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2023-02-09 fix: added no-connects
    [PSLab.kicad_sch]
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2023-02-09 fix: resolved all erc issues in schematic
    [PSLab.kicad_sch]
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2023-10-20 fix: resolved design rules issues and workflow
    [PSLab-B_Mask.gbr, PSLab-B_Paste.gbr, PSLab-B_Silkscreen.gbr, PSLab-Edge_Cuts.gbr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]
2023-12-02 fix: silk screen changes
    [BillOfMaterials.csv, PSLab-B_Mask.gbr, PSLab-B_Silkscreen.gbr, PSLab-F_Silkscreen.gbr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]
2023-12-03 fix: drc errors
    [PSLab-B_Mask.gbr, PSLab-B_Paste.gbr, PSLab-B_Silkscreen.gbr, PSLab-Edge_Cuts.gbr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]
2023-12-03 fix: silk screen
    [PSLab-B_Mask.gbr, PSLab-B_Paste.gbr, PSLab-B_Silkscreen.gbr, PSLab-Edge_Cuts.gbr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]
